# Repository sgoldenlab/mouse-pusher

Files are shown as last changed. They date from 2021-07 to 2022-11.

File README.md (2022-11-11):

# Mouse Pusher 

Mouse pusher is a complementary mechanical device for the med-pc operant boxes, to replace manual labor when propelling mice into the experiment arena.  Potentially, by freeing researcher from pushing multiple mice at the same time, the mouse pusher can improve efficiency and accuracy of the procedures and even reduce the audience effect on the mice. This design were tested in the aggression protocol at the Golden Lab UW. This is designed for extra wide operant box. 

## Demonstration video 

https://user-images.githubusercontent.com/50497030/128563699-18b8701d-70c7-49fd-a3ca-df1fa9bf6b25.mp4

## Wiring diagram of linear rail

For each mouse pusher, we need the following components below:

#### Components list 
- Arduino Uno
- L298N Motor Driver
- [Linear Stage Rail](https://www.amazon.com/Linear-Actuator-Stepper-Milling-Machine/dp/B07K7FQ245)
- Screws (based on your linear stage rail requirement) 
- 24V Power Adapter (for the stepper motor, might be different depends on the motor you have)
- 9V Power Adapter (for powering arduino separately) 
- Jumper wires
- Electrical tape





| Pin Name    | Description |
| ------------- | ------------- |
| OUT1 & OUT2  | Output pins of Motor A (A+ to OUT1, A- to OUT2 |
| OUT3 & OUT4  | Output pins of Motor B (B= to OUT3, B- to OUT2 |
| 12V / VCC    | power supply input, if > 12V DC, remove 12V jumper (black jumper in front of the input)|
| 5V | 5V pin on Arduino |
| GND | Ground pin |
| IN1 | pin 8 |
| IN2 | pin 9 |
| IN3 | pin 10 |
| IN4 | pin 11 |

### Step by Step assembling instruction 

For a single set, you need 1 linear stage rail, 1 arduino, 1 L298N, 4 M/M jumper wires, 4 M/F jumper wires, 1 9V power adapter, and 1 24V power adapter (with connector tip) 

Step 1: braid the wires from the linear stage rail 



Step 2: wrap electrical tape around the wire for protection



step 3: take out two sets of two male to male jumper wires, and a set of four male to female jumper wires.



step 4: wrap electrical tapes around jumper wires, we color coded them to distinguish different sets.



step 5: connect wires to l298N motor driver according to the table above 



step 6: connect wires to arduino according to the table above



step 7: connect the wire from 12V+ port from L298N to the positive on the adapter connector, and the ground to the negative on the adapter connector.



step 8: plug in 24V to L298N power adapter and 9V to arduino uno. 

Tp test the linear stage rail, use position adjustment script moving the stage to desired starting position, and use trial loop script to test stability for 10 minutes.

## Wiring connecting arduino and Med-PC

#### Components：

- 24V to 5V Optocoupler ( I used 8 channel ones for every 6 of the wire set, you can buy any type of optocoupler that suits best for your project requirement)  
- 5V power adapter 
- Wire
- Electrical tape



Optocoupler is used to step down the high voltage ttl signal from Med-PC to protect Arduino from frying. the signal output would go to Analog port on arduino (we used A3), and negative goes to the second ground on arduino.

## Code

### Arduino script

#### Operant box trial script 

  [Click here for Operant Box Trial Script](https://github.com/sgoldenlab/mouse-pusher/blob/522724d3c4da9a7dc0e854c799d4fd747f263456/Arduino%20Scripts/Trial_script.ino/Trial_script.ino.ino)

  This script is for running the actual operant box trials, detailed explanation in the script file, might need small modification to fit your specific trials. 

#### Linear stage position adjustment script

  [Click here for Linear stage position adjustment script](https://github.com/sgoldenlab/mouse-pusher/blob/522724d3c4da9a7dc0e854c799d4fd747f263456/Arduino%20Scripts/Position_adjustment_script.ino/Position_adjustment_script.ino.ino)

  This script can be used to move the stage to the preferred starting position, or if stalling problem happens, can be used to do some quick testing for the specific reason for stalling

#### Testloop script 

  [Click here for testloop script](https://github.com/sgoldenlab/mouse-pusher/blob/522724d3c4da9a7dc0e854c799d4fd747f263456/Arduino%20Scripts/Testloop_script.ino/Testloop_script.ino.ino)

  We use this script to test if the wired pusher set is stable before installing it on the opearnt box. This script is optional but we found it useful to prevent the hassel of fixing it after the set being attached to the opearnt box. 

### Med-PC code

[Click Here for example for the Med_PC code](https://github.com/sgoldenlab/mouse-pusher/blob/7db21a7be5d829b1ad788d06850c045fe5f82429/MedPc%20code.MPC)

The code above is the Medpc script we used for self-administration aggression study, on the foundation of the original script,
We added ^Pusher = 14 (or any open output number you have) to Outputs sections,
then at the codes where you command for output to open the door, we added ON ^Pusher
Same where you command for output to close the door, we added OFF ^Pusher

Here are the examples clipped from the script above: 





## STL Models

[Click here to see display model for all components together](https://github.com/sgoldenlab/mouse-pusher/blob/main/STL%20files/assemble.stl)

### [Chamber Body](https://github.com/sgoldenlab/mouse-pusher/blob/main/STL%20files/chamber.stl) 



The chamber body would be the structure to contain the mice before they are pushed into the operant box, it can contain two mice at a time so the intruder mice can rotate and not getting thrown into the arean as frequently.

### [Pole](https://github.com/sgoldenlab/mouse-pusher/blob/main/STL%20files/separated_pole.stl)



The pole is attached to the linear stage, through screw in the four holes, the side with longer side being towards the back of the linear stage. Modification might be needed if the stage has different dimensions.

### [Bottom 1](https://github.com/sgoldenlab/mouse-pusher/blob/main/STL%20files/bottom1.stl) 



This is the first detachable bottom of the two, they can be fitted together into the gap at the bottom of the chamber 

### [Bottom 2](https://github.com/sgoldenlab/mouse-pusher/blob/main/STL%20files/bottom2.stl)



This is the second detachable bottom of the two, they can be fitted together into the gap at the bottom of the chamber. We have designed the bottoms to be thinner and narrower than the gap of the chamber, but due to 3d printer's accuracy, it might still be hard to fit in or remove them. The little wedge on the second bottom can help you grip it better, and makes it easier to remove this bottome first. If hand strength not enough, please try a plier. If still not fitting correctly, some decrease in width and length might be needed. 

### [Pusher Plate](https://github.com/sgoldenlab/mouse-pusher/blob/main/STL%20files/pusherplate.stl) 



The pusher plate is going to be attached onto the pole, the side with shorter legs being the inward side. 

### [Supporting Foundation](https://github.com/sgoldenlab/mouse-pusher/blob/main/STL%20files/SupportU.stl)



This structure is being attached to the operant box under the chamber. the vertical thin flat surface can be fit in the same gap we use to attach the chamber body. the supporting foundation would make all the chamber body be on the same height and restrict unnecessary movement of the linear rail. Depends on the stability of your operant box, the support foundation might still be able to move around a lot, you can use tape to secure the side to the operant box. (If linear rail not the same dimensions, modification would be needed)

### [Rotate Block](https://github.com/sgoldenlab/mouse-pusher/blob/main/STL%20files/rotate.stl)



The rotate block is a 2 piece structure that would be fitted together through the round hole on the chamber body, when putting down after the divider is in, it would prevent the divider being moved out by the mice. 

### [Divider](https://github.com/sgoldenlab/mouse-pusher/blob/main/STL%20files/divider.stl) 



The divider fits in highest horizontal gap to separate the two mice in the chamber, when fitting in appropriately into the back slot on the other side of the chamber, the thin line on divider should be close to the surface of the chamber.

### [Rail Guard](https://github.com/sgoldenlab/mouse-pusher/blob/main/STL%20files/railblock.stl) 



The Rail guard is a barrier for the tail preventing debris or mice feces getting into the linear stage rail. This stl file is upside down for easier printing purpose.

## Common problems

1. Linear stage rail moves, causing the pusher plate or pole getting stuck by the chamber or other structure around the operant box. 

Solution: if stuck in the middle and not returning to the start position, use position adjustment script to return the stage back into starting position, and check for broken components, replace if needed. 

2. Not moving after wiring, often along with strange noise 

Solution: recheck all wiring to see if they are all in place, if they are, check if the right voltage of power adapted is connected. If still not solved, check the voltage reading from your mouse pusher script, if the voltage doesn't change to 1023 when you open output 14, it means there is no connection between arduino and medpc, you need to change wire or replug it. 

## Precautions

Turning off when not using, especially before closing operant box, turning of operant box first will lead to all boxes push forward because the voltage change by the optocoupler 

Our advice is to have some backup parts because before everything is properly installed and stablized, it might be very easy to break thin parts like poles and rotate block. 

#### Warning: Divider must be properly locked in and not able to be lodged off, or mice can possibly be serioudly injured.

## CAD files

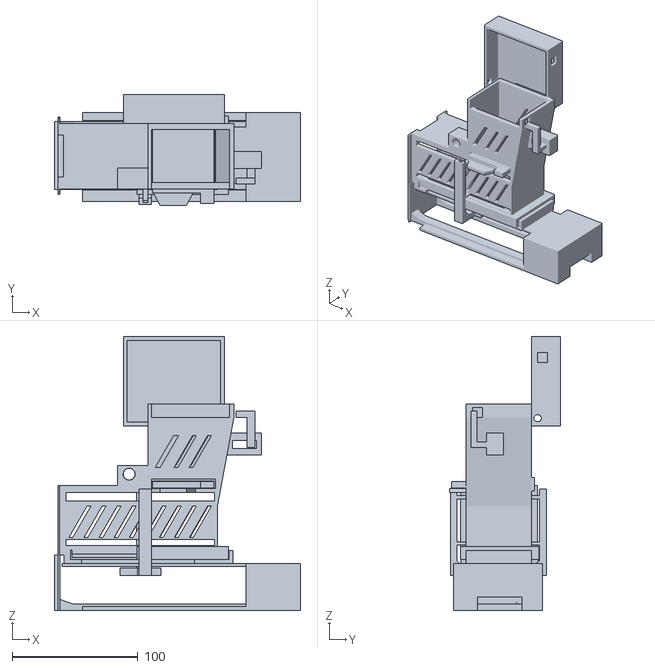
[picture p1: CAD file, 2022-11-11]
STL files/assemble.stl
195.6 x 87.8 x 217.5

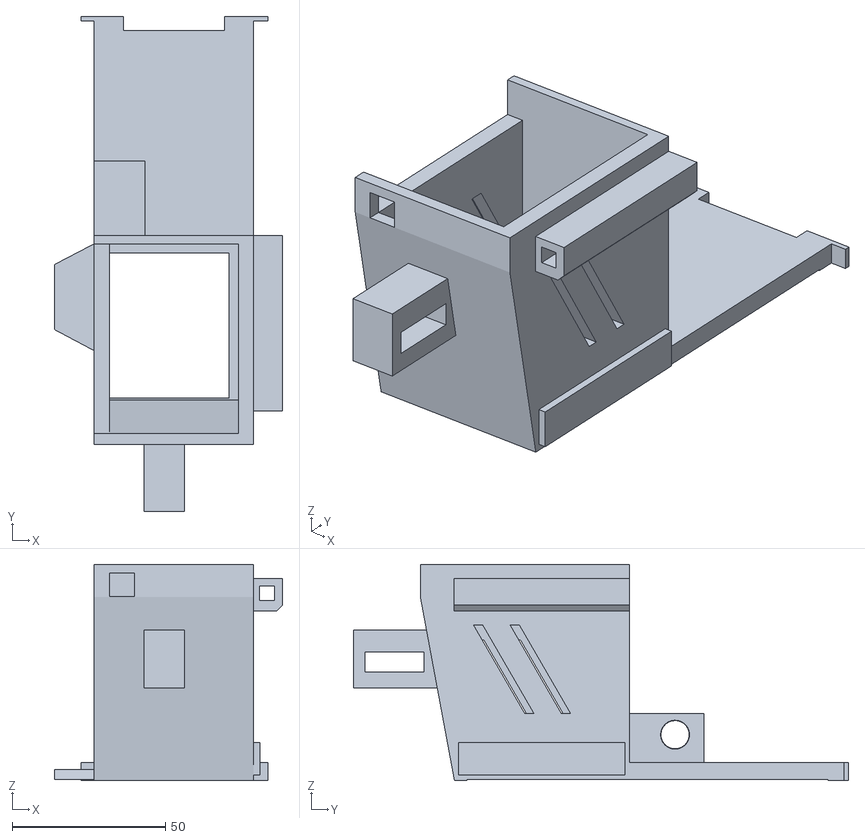
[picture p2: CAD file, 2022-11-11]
STL files/Topchamber.stl
74.5 x 161.6 x 70.6

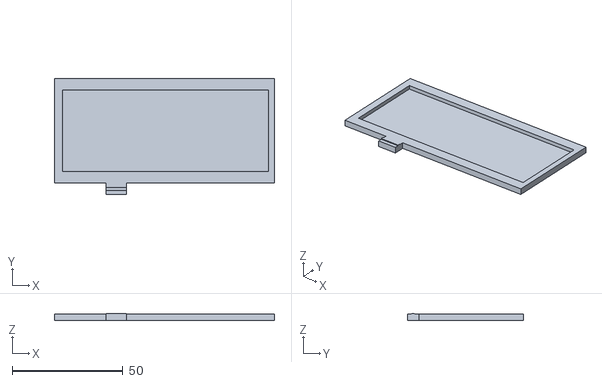
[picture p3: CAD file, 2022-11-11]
STL files/bottom2.stl
99.4 x 52.5 x 3.26

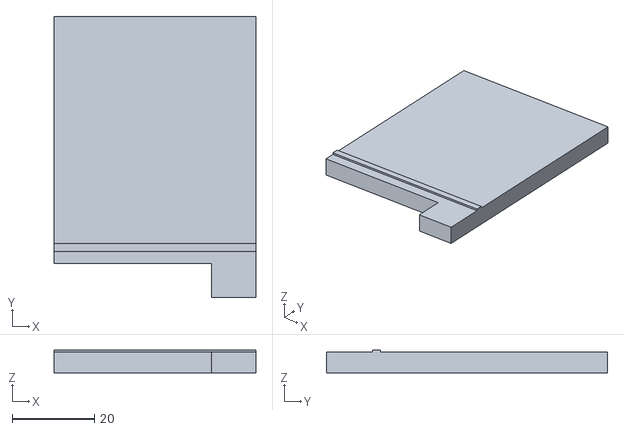
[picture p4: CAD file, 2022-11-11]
STL files/divider.stl
49.0 x 68.3 x 5.50

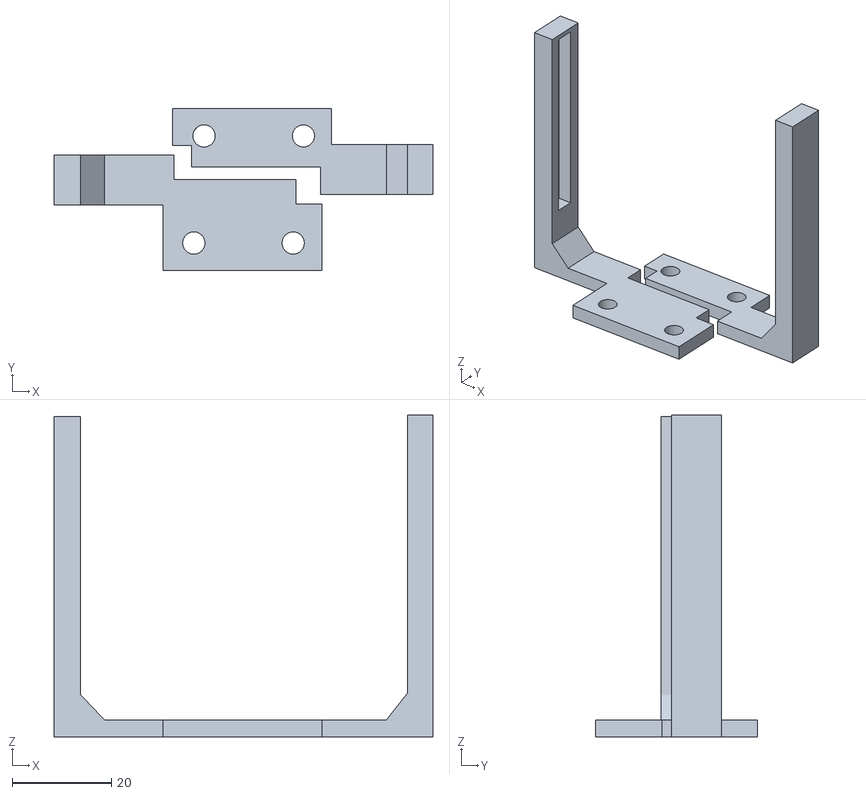
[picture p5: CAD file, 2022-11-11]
STL files/separated_pole.stl
76.3 x 32.5 x 64.8

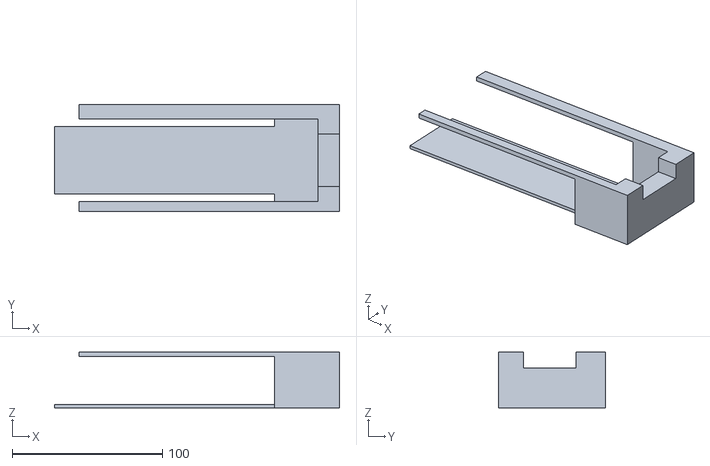
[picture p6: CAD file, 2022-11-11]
STL files/railblock.stl
189.5 x 70.9 x 37.2

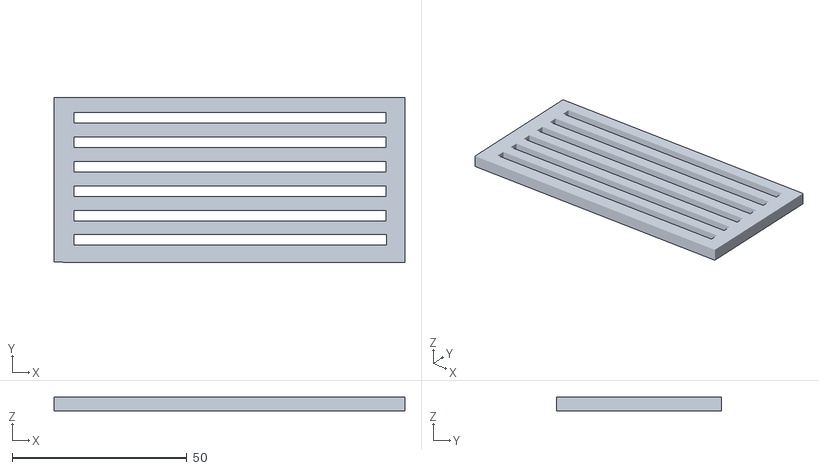
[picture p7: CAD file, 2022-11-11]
STL files/bottom1.stl
100.4 x 47.2 x 3.95

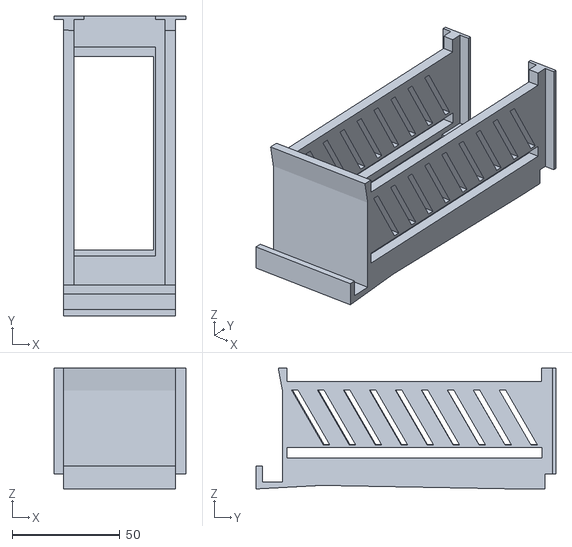
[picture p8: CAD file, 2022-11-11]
STL files/bottomchamber.stl
61.0 x 138.9 x 56.0

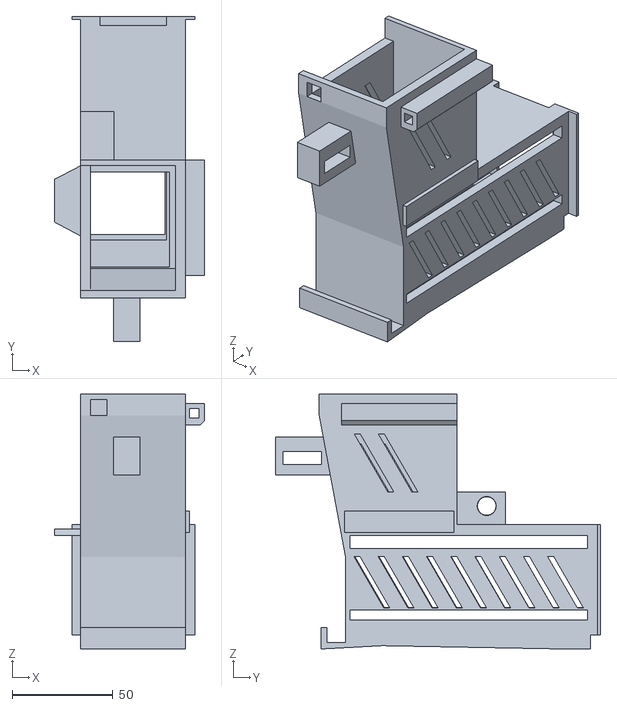
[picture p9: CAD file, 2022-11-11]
STL files/chamber.stl
74.5 x 161.6 x 126.6

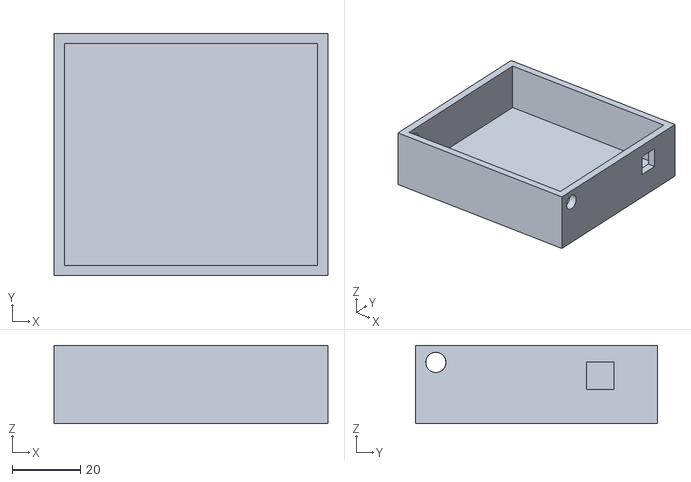
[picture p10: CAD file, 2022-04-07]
STL files/Lid.stl
80.3 x 71.0 x 23.0

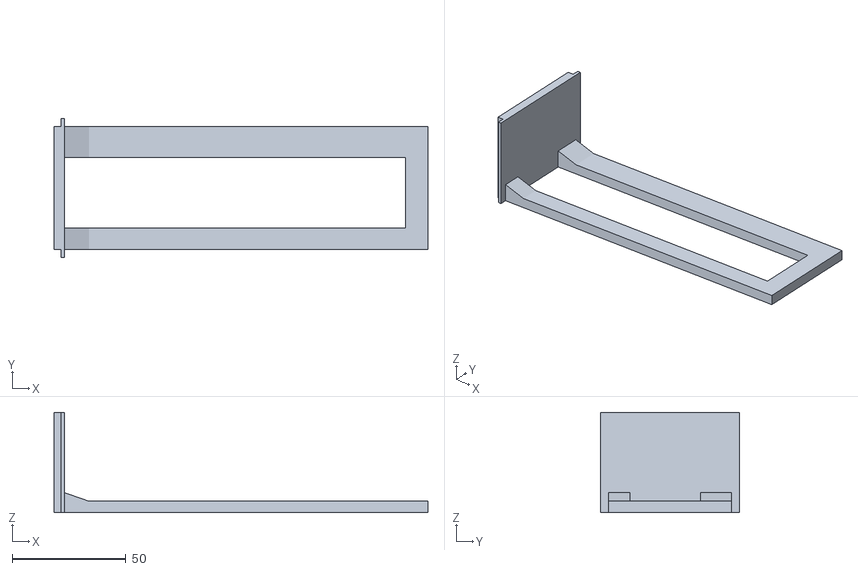
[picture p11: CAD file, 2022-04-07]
STL files/SupportU.stl
164.5 x 61.0 x 44.0

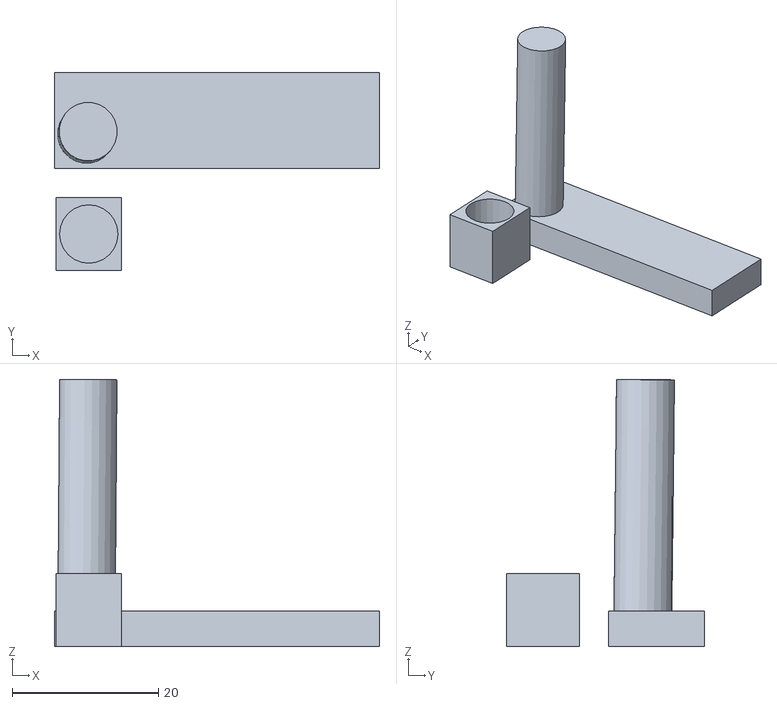
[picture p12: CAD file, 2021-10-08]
STL files/rotate.stl
44.5 x 27.1 x 36.6

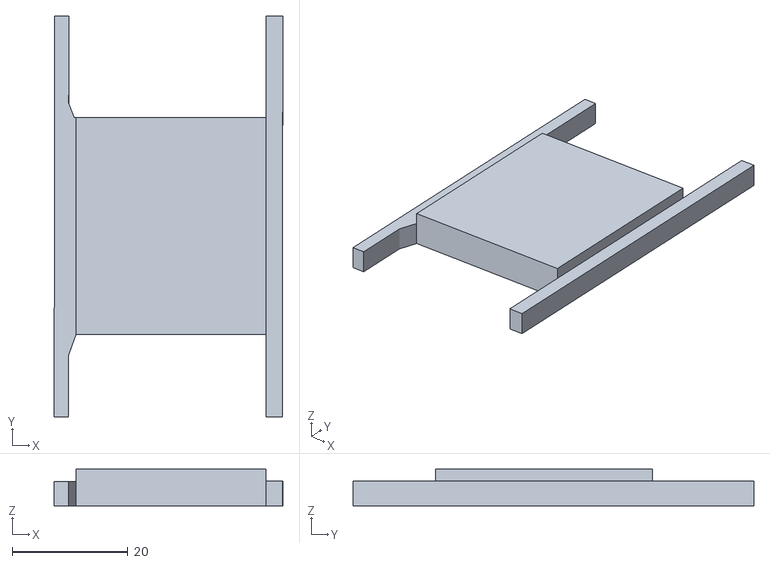
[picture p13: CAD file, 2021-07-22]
STL files/pusherplate.stl
39.5 x 69.2 x 6.37

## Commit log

2021-10-15 Rename thinner divider.stl to Divider.stl
    [Divider.stl]
2022-04-07 Create Chamber_updated
